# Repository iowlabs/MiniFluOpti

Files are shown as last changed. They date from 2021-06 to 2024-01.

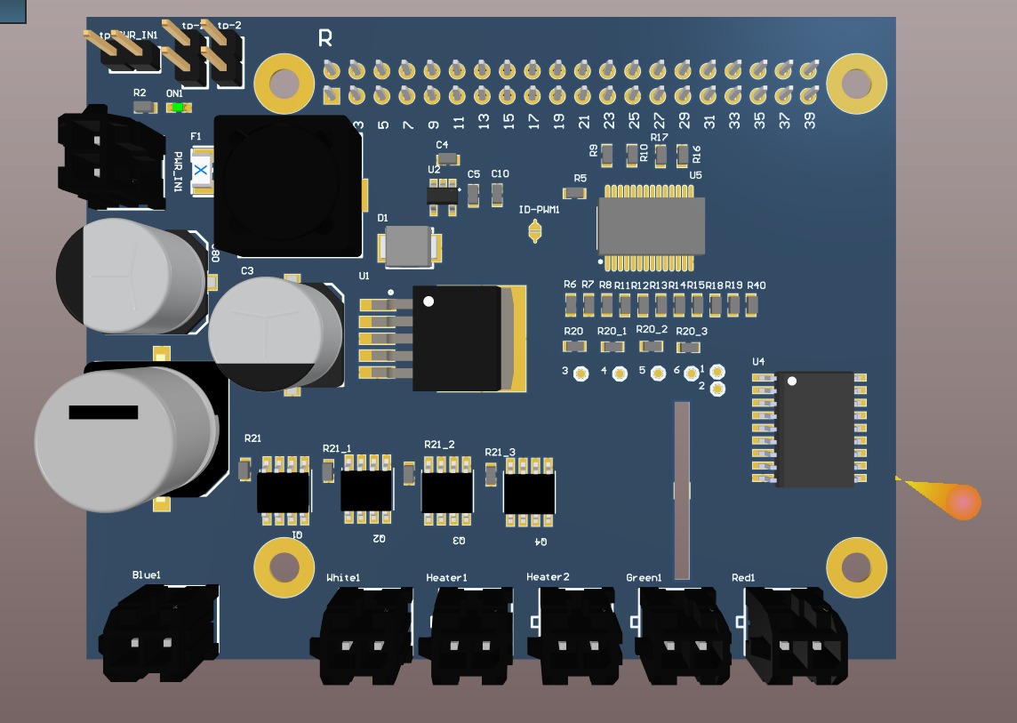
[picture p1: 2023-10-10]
hardware/Enclosure/Placa_esquematico.jpg

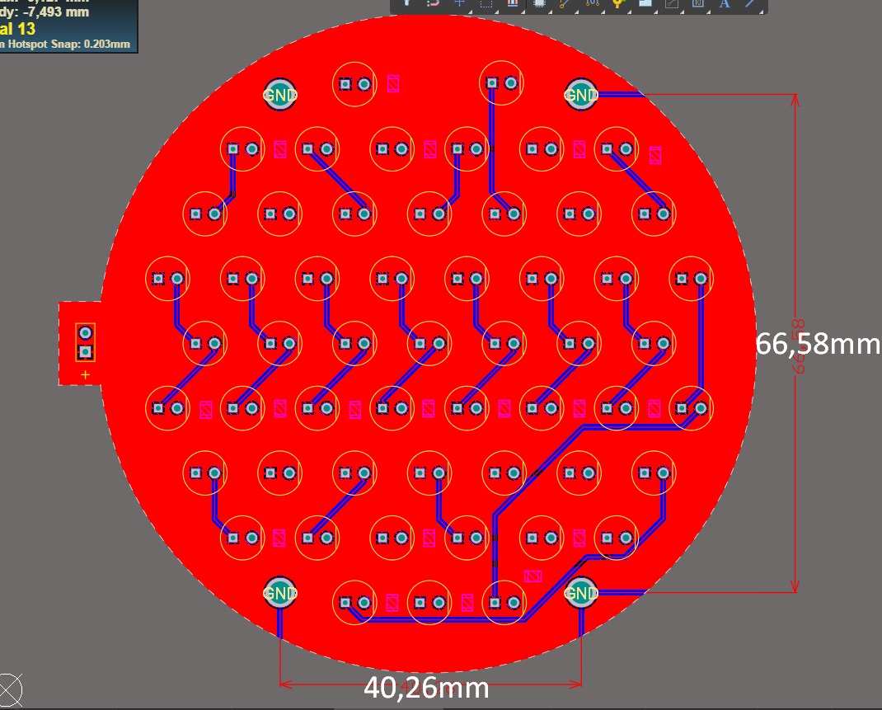
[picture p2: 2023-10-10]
hardware/Enclosure/Circle_LEDS_PCB.jpg

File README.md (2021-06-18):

# MiniFluOpti

Versión mini del proyecto FluOpti. Desarrollo conjunto con equipo docente del Instituto de Ingeniería Biológica UC. 
Este proyecto consiste en un controlador de LEDs configurable por I2C. La placa controla 4 canales controladores de LEDs, por medio de señales PWM generadas *on-board*. Los grupos de LEDs considerado para esta versión son: rojos, verde, azul y blanco. Adicionalmente la placa 
incluye un controlador de *heater* y un par de canales de lectura de sensores de temperatura del tipo termistor.

## Características:

* Voltaje de entrada 12[V].
* 4 Canales de salida LEDs: Rojo, Verde, Azul, Blanco.
* 1 Controlador de heater. Max: 12[V] - 3[A]
* 2 Canales de lector de termistor.
* Voltaje de salida para alimentar Rpi 5[V] 2.5[A] (Raspy 3b+)
* Voltaje en placa 3.3[V] para componentes digitales.
* Voltajes disponibles: 3.3[V] 5[V], 9[V] y 12[V]
* Protocolo de control: I2C (deseado)
 
Dependencias:
* Generador de PWMs PCA9685
* Drivers de corriente IRF740
* Drivers de baja corriente (500mA) ULN2803A
* Lector de termistor MAX6682
* Reguladores de voltaje
* Conversores DC-DC

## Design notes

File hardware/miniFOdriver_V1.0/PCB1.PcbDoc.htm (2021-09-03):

Reporting Options

# File in Newer Format

Date | : | 02-09-2021
Time | : | 23:33:18
Filename | : | C:\Users\Wac\Desktop\repo_pega\iowlabs\MiniFluOpti\3 - Hardware\miniFOdriver_V1.0\PCB1.PcbDoc

Version | Warning
Release 20.0 | CAUTION - Support of propagation delay for primitives
Release 20.0 | CAUTION - Support for PCB system parameters, used to contain additional data extracted from components

This file was generated by a later version of the software

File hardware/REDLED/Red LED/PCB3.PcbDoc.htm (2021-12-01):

Reporting Options

# File in Newer Format

Date | : | 19-10-2021
Time | : | 16:37:40
Filename | : | C:\Users\Wac\Desktop\repo_pega\iowlabs\MiniFluOpti\3 - Hardware\REDLED\Red LED\PCB3.PcbDoc

Version | Warning
Release 20.0 | CAUTION - Support of propagation delay for primitives
Release 20.0 | CAUTION - Support for PCB system parameters, used to contain additional data extracted from components

This file was generated by a later version of the software

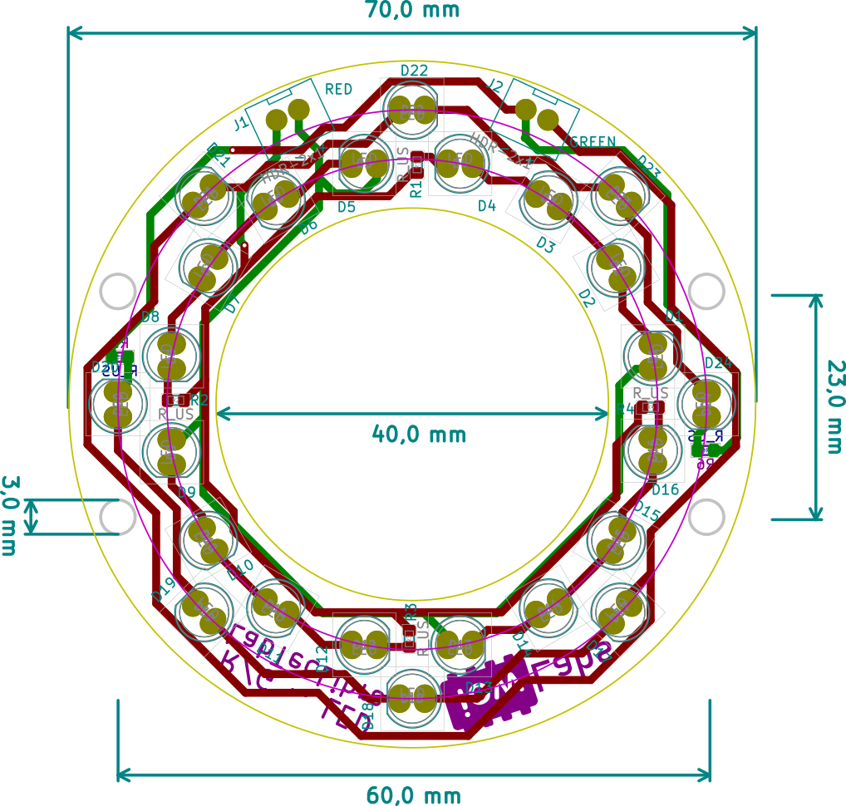
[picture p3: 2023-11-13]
hardware/GREENRED_LED/RG_Led_ring-brd.png

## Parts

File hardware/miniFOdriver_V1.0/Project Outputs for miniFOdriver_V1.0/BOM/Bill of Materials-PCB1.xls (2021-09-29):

Description | Designator | Footprint | Supplier Part Number 1 | Quantity | Supplier 1 | Value
Electrolytic Aluminium Capacitor | C2 | CAP_SMD_Electrolytic_10x10 | C178568 (https://octopart-clicks.com/click/altium?manufacturer=Panasonic&mpn=EEE-FK1V681AQ&seller=LCSC&sku=C178568&country=CL&channel=BOM%20Report) | 1 | LCSC | 680uF
Electrolytic Aluminium Capacitor | C3 | CAP_SMD_Electrolytic_10x10 | C249650 (https://octopart-clicks.com/click/altium?manufacturer=Loading...&mpn=Loading...&seller=LCSC&sku=C249650&country=CL&channel=BOM%20Report) | 1 | LCSC | 330uF
Capacitor (Semiconductor SIM Model) | C4, C5 | 1608[0603] | C59782 (https://octopart-clicks.com/click/altium?manufacturer=Samsung&mpn=CL10B105KO8NNNC&seller=LCSC&sku=C59782&country=CL&channel=BOM%20Report) | 2 | LCSC | 1uF
Capacitor (Semiconductor SIM Model) | C10 | 1608[0603] | C92487 (https://octopart-clicks.com/click/altium?manufacturer=Samsung&mpn=CL10A106MO8NQNC&seller=LCSC&sku=C92487&country=CL&channel=BOM%20Report) | 1 | LCSC | 10uF
Capacitor (Semiconductor SIM Model) | C12, C13 | 1608[0603] | C66501 (https://octopart-clicks.com/click/altium?manufacturer=Samsung&mpn=CL10B104KO8NNNC&seller=LCSC&sku=C66501&country=CL&channel=BOM%20Report) | 2 | LCSC | 100nF
Electrolytic Aluminium Capacitor | C80 | CAP_SMD_Electrolytic_5X5.4 |  | 1 | LCSC | 47uF
Schottky Diodes | D1 | SMB_L4.6-W3.6-LS5.3-RD | C180191 (https://octopart-clicks.com/click/altium?manufacturer=Loading...&mpn=Loading...&seller=LCSC&sku=C180191&country=CL&channel=BOM%20Report) | 1 | LCSC
Generic LED SMD | D2, D3, D4 | LED0603 | C72043 (https://octopart-clicks.com/click/altium?manufacturer=Loading...&mpn=Loading...&seller=LCSC&sku=C72043&country=CL&channel=BOM%20Report) | 3 | LCSC
SMD Fuse | F1 | F1206 | C310980 (https://octopart-clicks.com/click/altium?manufacturer=Loading...&mpn=Loading...&seller=LCSC&sku=C310980&country=CL&channel=BOM%20Report) | 1 | LCSC
solder jumper generic | ID-PWM1 | SJ2 |  | 1
Generic Header 2pos, 1 row, 2.54 pitch | J1, J2, J3, J4, J5, J6, J7, J8 | JST-2x1 | C20079 (https://octopart-clicks.com/click/altium?manufacturer=Loading...&mpn=Loading...&seller=LCSC&sku=C20079&country=CL&channel=BOM%20Report) | 8 | LCSC
Screw terminal 2pos, 1 row, 5pitch | J9 | T_BLOCK_2P | C8404 (https://octopart-clicks.com/click/altium?manufacturer=Kangnex&mpn=WJ126V-5.0-2P&seller=LCSC&sku=C8404&country=CL&channel=BOM%20Report) | 1 | LCSC
Inductor SMD | L1 | IND-SMD_L12.5-W12.5_SMDRS1275 | C439422 (https://octopart-clicks.com/click/altium?manufacturer=Loading...&mpn=Loading...&seller=LCSC&sku=C439422&country=CL&channel=BOM%20Report) | 1 | LCSC | 33uH
MOSFET N Channel 20V 8.7A 700mV @ 250uA 22mΩ @ 4.1A,4.5V SOIC-8_150mil RoHS | Q1, Q2, Q3, Q4 | SOIC8 | C169089 (https://octopart-clicks.com/click/altium?manufacturer=Infineon&mpn=IRF7402TRPBF&seller=LCSC&sku=C169089&country=CL&channel=BOM%20Report) | 4 | LCSC
GPIO Header for Raspberry Pi A+/B+/Pi 2/Pi 3 - 2x20 | R | rpi | 1568-1462-ND (https://octopart-clicks.com/click/altium?manufacturer=Loading...&mpn=Loading...&seller=LCSC&sku=1568-1462-ND&country=CL&channel=BOM%20Report) | 1 | LCSC
±1% ±100ppm/℃ 0.1W 220Ω 0603 Chip Resistor - Surface Mount ROHS, Resistor, Resistor, Resistor, Resistor, Resistor, Resistor | R1, R13, R14, R15, R18, R19, R40 | J1-0603 | C304718 (https://octopart-clicks.com/click/altium?manufacturer=Loading...&mpn=Loading...&seller=LCSC&sku=C304718&country=CL&channel=BOM%20Report) | 7 | LCSC | 220
Resistor | R2 | J1-0603 | C23057 (https://octopart-clicks.com/click/altium?manufacturer=Loading...&mpn=Loading...&seller=LCSC&sku=C23057&country=CL&channel=BOM%20Report) | 1 | LCSC | 442
Resistor | R3 | J1-0603 | C114608 (https://octopart-clicks.com/click/altium?manufacturer=Loading...&mpn=Loading...&seller=LCSC&sku=C114608&country=CL&channel=BOM%20Report) | 1 | LCSC | 150
Resistor | R5, R8, R9, R10, R11, R12 | J1-0603 | C105576 (https://octopart-clicks.com/click/altium?manufacturer=Loading...&mpn=Loading...&seller=LCSC&sku=C105576&country=CL&channel=BOM%20Report) | 6 | LCSC | 2K
Resistor | R6, R7, R16, R17 | J1-0603 | C441927 (https://octopart-clicks.com/click/altium?manufacturer=Panasonic&mpn=ERJPA3F1002V&seller=LCSC&sku=C441927&country=CL&channel=BOM%20Report) | 4 | LCSC | 10K
Resistor | R20, R20_1, R20_2, R20_3 | J1-0603 | C22781 (https://octopart-clicks.com/click/altium?manufacturer=Loading...&mpn=Loading...&seller=LCSC&sku=C22781&country=CL&channel=BOM%20Report) | 4 | LCSC | 110
Resistor | R21, R21_1, R21_2, R21_3 | J1-0603 | C25804 (https://octopart-clicks.com/click/altium?manufacturer=Uniroyal&mpn=0603WAF1002T5E&seller=LCSC&sku=C25804&country=CL&channel=BOM%20Report) | 4 | LCSC | 10K
 | R22, R23 | RESC1609X50X30LL10T20 | C170595 (https://octopart-clicks.com/click/altium?manufacturer=Loading...&mpn=Loading...&seller=LCSC&sku=C170595&country=CL&channel=BOM%20Report) | 2 | LCSC | 4.22k
Pin Header 2pos, 1 row, 2.54 pitch | tp-1, tp-2, tp-PWR_IN1 | HDR-TH_P2.54-H-M_A2541WV-2P | C492401 (https://octopart-clicks.com/click/altium?manufacturer=Loading...&mpn=Loading...&seller=LCSC&sku=C492401&country=CL&channel=BOM%20Report) | 3 | LCSC
Step-Down Positive Fixed 1 3A 150kHz TO-263-5 DC-DC Converters RoHS | U1 | TO-263-5 | C77782 (https://octopart-clicks.com/click/altium?manufacturer=Loading...&mpn=Loading...&seller=LCSC&sku=C77782&country=CL&channel=BOM%20Report) | 1 | LCSC
600mA CMOS LDO REGULATOR WITH ENABLE | U2 | SOT25-5 | C150742 (https://octopart-clicks.com/click/altium?manufacturer=Diodes&mpn=AP7365-33WG-7&seller=LCSC&sku=C150742&country=CL&channel=BOM%20Report) | 1 | LCSC
Darlington transistor array driver SOIC-18_300mi | U4 | SOIC18 | C33924 (https://octopart-clicks.com/click/altium?manufacturer=Loading...&mpn=Loading...&seller=LCSC&sku=C33924&country=CL&channel=BOM%20Report) | 1 | LCSC
LED Drivers,16CH, I2C, TSSOP-28 | U5 | SSOP-28_L | C92206 (https://octopart-clicks.com/click/altium?manufacturer=NXP%20Semiconductors&mpn=PCA9685PW%2FQ900%2C118&seller=LCSC&sku=C92206&country=CL&channel=BOM%20Report) | 1 | LCSC
Thermistor-to-Digital Converter, 10 Bits Temperature Resolution, -55 to 125 degC, 8-Pin SOP (U8+1), Pb-Free, Tape and Reel | U6, U7 | MAXM-U8+1_L | C2653145 (https://octopart-clicks.com/click/altium?manufacturer=Loading...&mpn=Loading...&seller=LCSC&sku=C2653145&country=CL&channel=BOM%20Report) | 2 | LCSC

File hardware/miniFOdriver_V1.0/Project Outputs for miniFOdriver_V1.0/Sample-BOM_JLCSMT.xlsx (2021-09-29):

Comment | Designator | Footprint | JLCPCB Part #（optional）
100uF | C1 | CAP-SMD_L3.5-W2.8 | C16133
15K | R5,R6 | R0603 | C22809
DC-005-20A_C136744 | DC1 | DC-IN-TH_DC-005-20A | C136744
Header-Female-2.54_1x8 | P2,P3 | HDR-TH_8P-P2.54-V | C27438
K2-1102DP-C4SW-04 | SW1 | KEY-TH_4P-L6.0-W6.0-P4.50-LS6.5 | C110153
ATMEGA328P-PU | U1 | DIP-28_L34.6-W7.3-P2.54-LS10.2-BL | C33901
670688000 | USB1 | USB-B-TH_67068-8000 | C114097

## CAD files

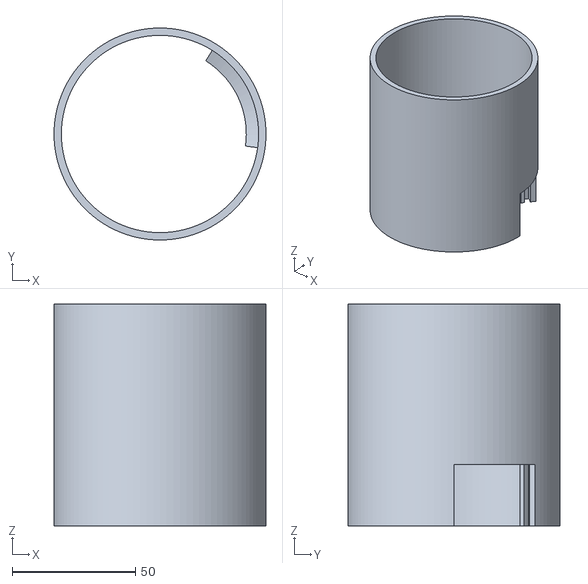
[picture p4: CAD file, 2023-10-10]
hardware/Enclosure/main_tube.stl
86.0 x 86.0 x 90.0

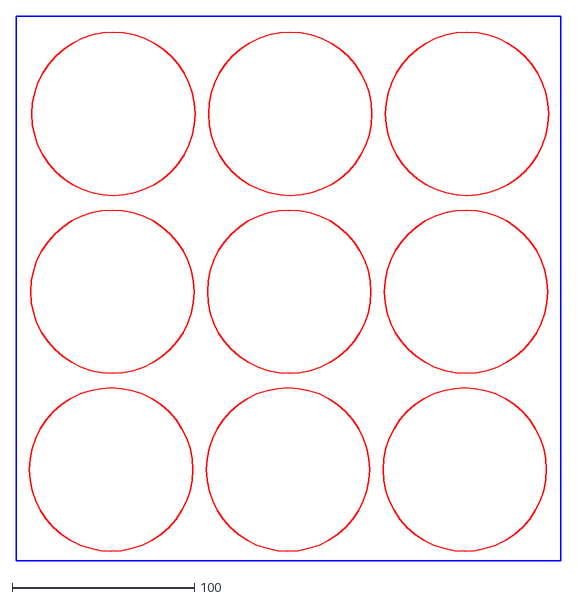
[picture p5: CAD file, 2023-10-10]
hardware/Enclosure/filters/blue_filtros.dxf
298.8 x 298.8

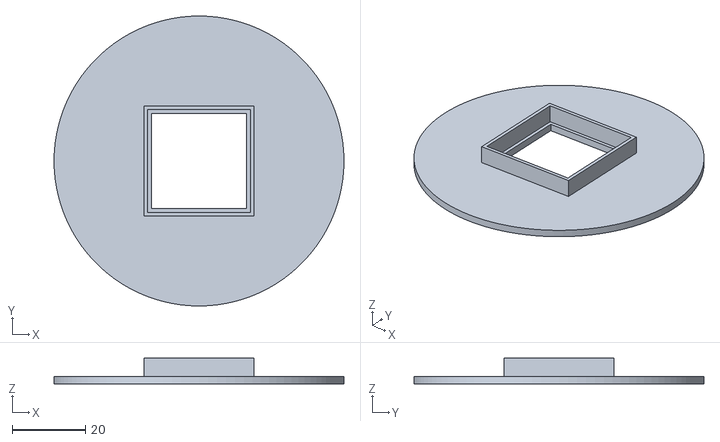
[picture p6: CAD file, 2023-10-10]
hardware/Enclosure/sample_holder_3x3.stl
79.0 x 79.0 x 7.00

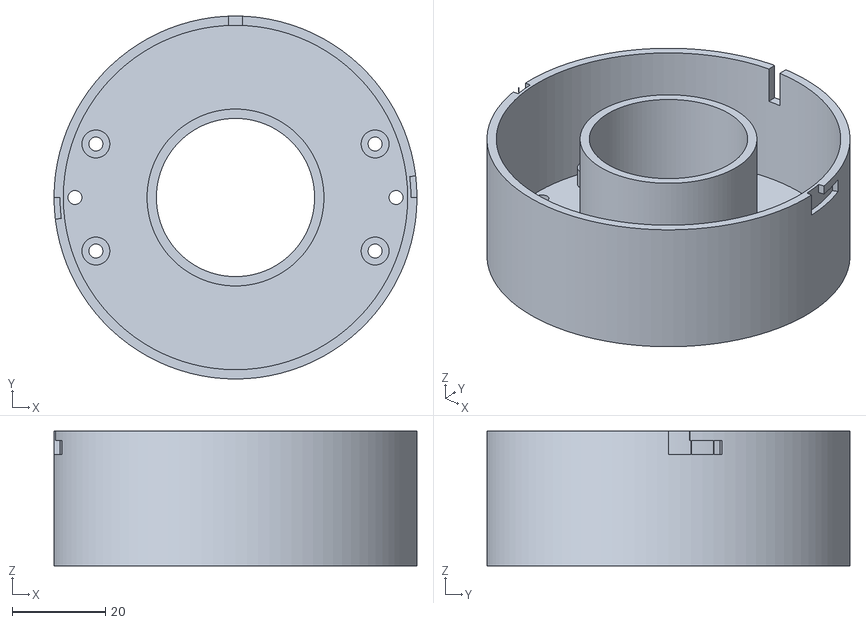
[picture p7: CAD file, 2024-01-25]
hardware/Enclosure/Soportes camara/STLs/Ring_enclosure.stl
78.0 x 78.0 x 29.0

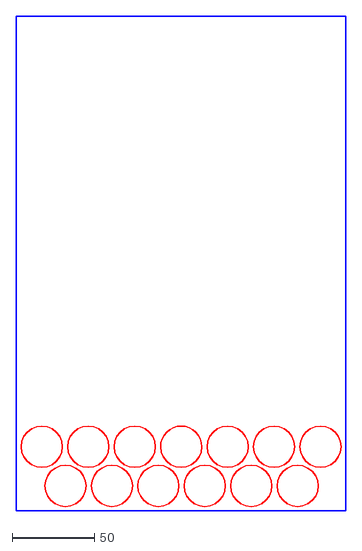
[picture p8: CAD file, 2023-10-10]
hardware/Enclosure/filters/ambar_filtros_13.dxf
200.0 x 300.0

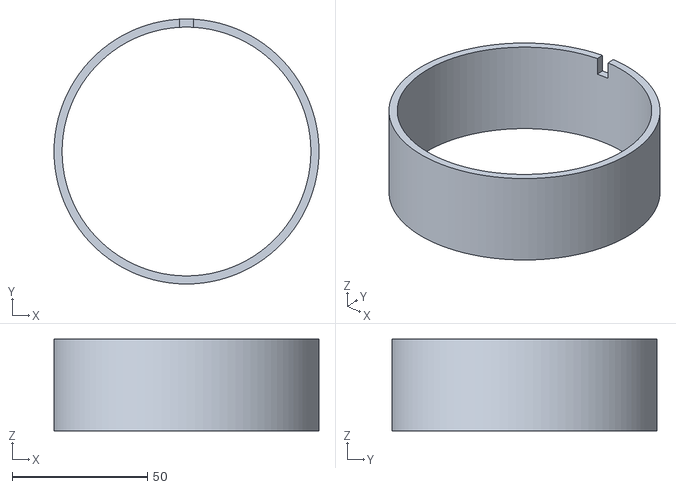
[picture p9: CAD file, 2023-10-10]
hardware/Enclosure/light_spacer.stl
98.0 x 98.0 x 34.0

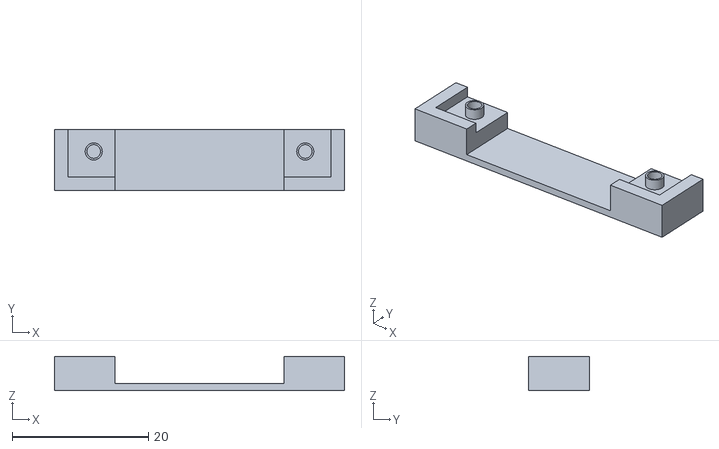
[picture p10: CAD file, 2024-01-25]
hardware/Enclosure/Soportes camara/STLs/HQ_test.stl
42.5 x 9.00 x 5.00

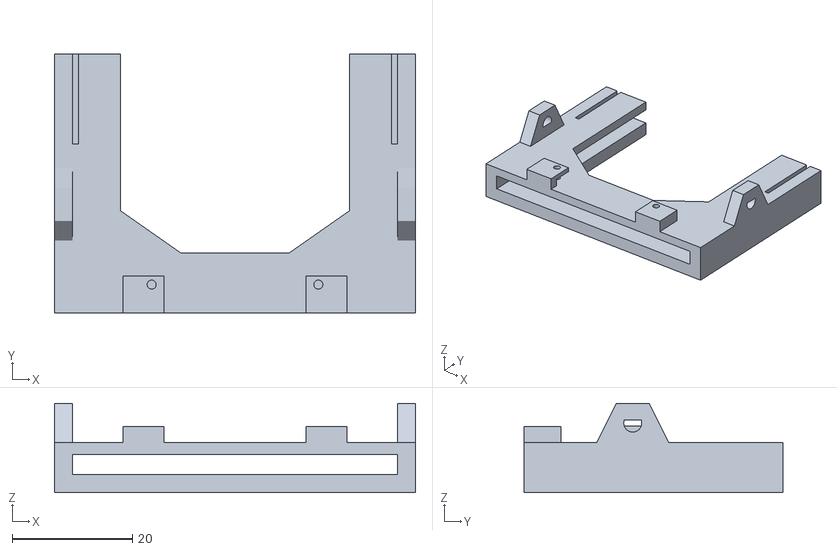
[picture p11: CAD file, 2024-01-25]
hardware/Enclosure/Soportes camara/STLs/Flat_cam_holder_WS_2.stl
60.0 x 43.1 x 14.8

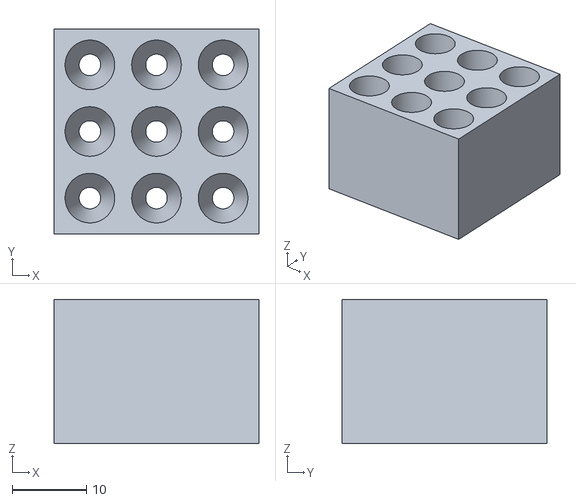
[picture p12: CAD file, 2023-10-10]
hardware/Enclosure/t_holder_3x3.stl
27.7 x 27.7 x 19.5

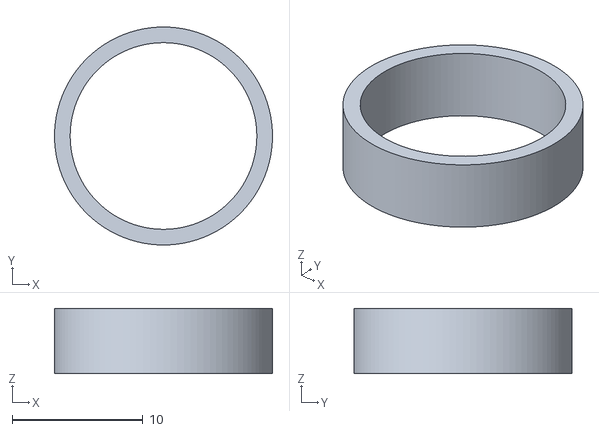
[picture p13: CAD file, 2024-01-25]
hardware/Enclosure/Soportes camara/STLs/M12_junction_test.stl
16.7 x 16.7 x 5.00

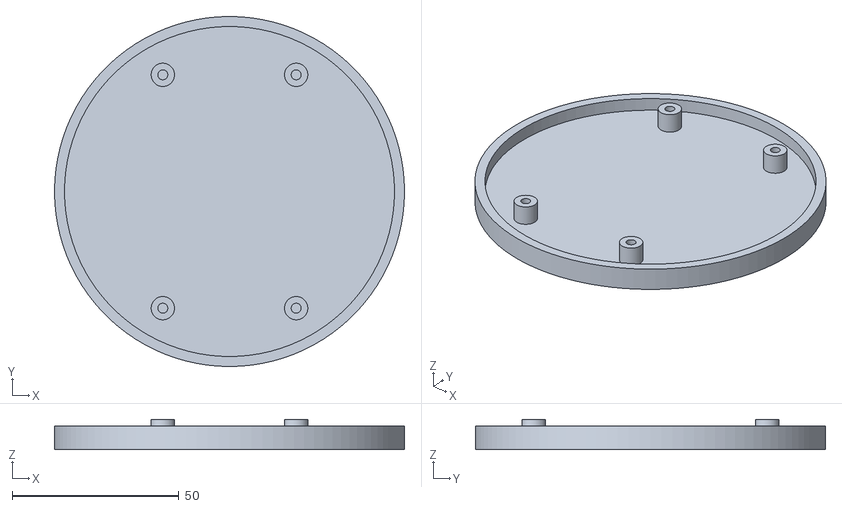
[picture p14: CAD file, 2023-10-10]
hardware/Enclosure/light_support.stl
105.0 x 105.0 x 9.00

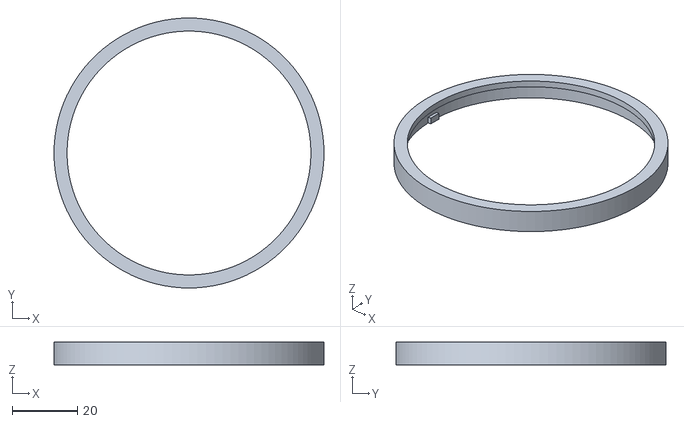
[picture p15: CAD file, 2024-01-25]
hardware/Enclosure/Soportes camara/STLs/outer_dring.stl
82.6 x 82.6 x 7.00

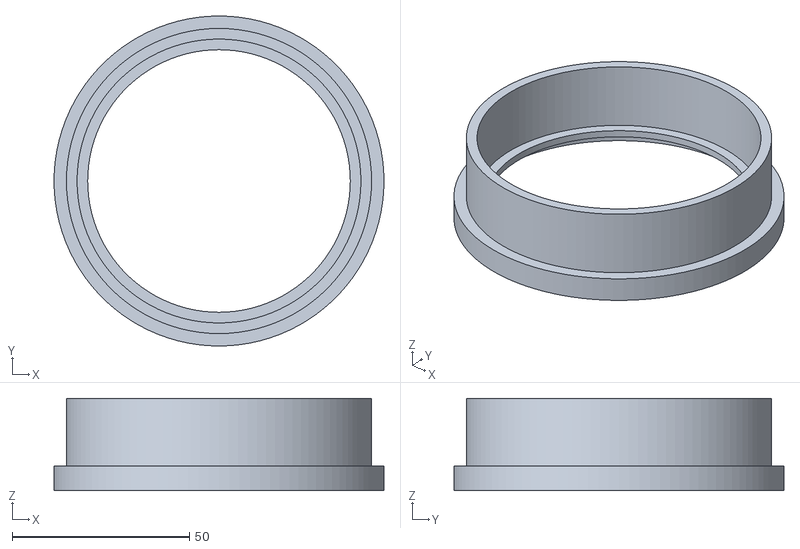
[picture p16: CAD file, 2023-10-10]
hardware/Enclosure/sample_tube.stl
93.0 x 93.0 x 26.0

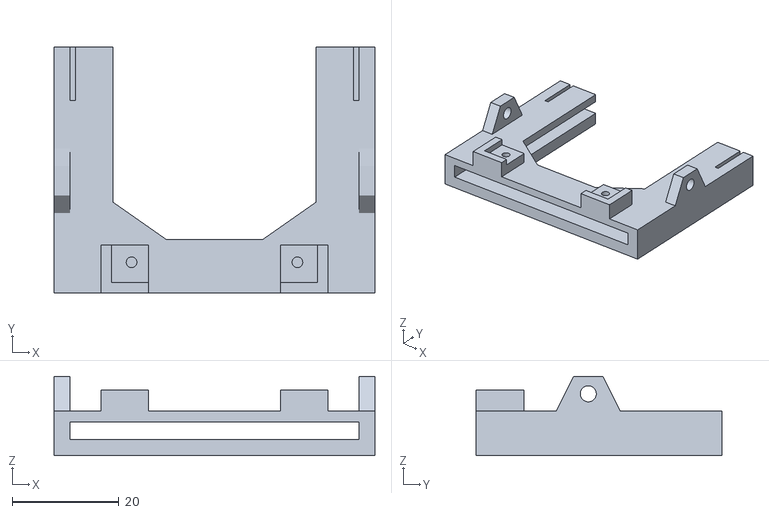
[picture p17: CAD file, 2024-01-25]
hardware/Enclosure/Soportes camara/STLs/Flat_cam_holder_HQ.stl
60.0 x 46.0 x 14.8

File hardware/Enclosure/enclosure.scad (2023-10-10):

/*
@Prosimio 2021

This is the Mini-FluOpti enclosure.

*/

////////////////
// Parameters //
////////////////


// general

id = 80;  // Internal diameter
ir = id/2; // internal radious

wt = 3;    // General wall thickness


// main tube 
os = 55;        // optical_space
cs = 35;        // camera_space
h1 = os + cs;   // main tube height
ha = 25;        // aperture height
h_door = ha + 4;  // door heigth
pih = h_door;       // pocket internal height
aa = 50;        // aperture angle [degrees]
pit = 3;        // pocket internal tickness
pet = 2;        // pocket external tickness
pia = 5;        // pocket internal angle [degrees]
pta = 3;        // pocket thickness angle [degrees]
ah = 10;        // door handle angle [degrees]

// sample tube
sh = 5;         // sheet height
st = 2;         // sheet support thickness
it = 3;         // internal sheet length
h2 = 21;        // tube height


// sample holder
hdt = 2;          // holder disk height
sst = 2;        // sample support sheet length
th = 2;         // barrier thickness horizontal
thz = 5;        // barrier thickness vertical       
xh = 28 ;   // x sample size + looseness if necessary
yh =  28 ;  // y sample size

// diffuser + filter support
f_t = 3;     // acrylic filter thickness
f_r = 45;        // filter radious
hd2 = 8;              // down mouting sheet heigh
hd1 = f_t + hd2;   // up mouting sheet heigh 
td = 2;                 // suppor disk thickness
ids = 1;                // internal disk sheet length
h3 = hd1 + hd2 + td;         // total piece height

// Light spacer
PCB_D = 90;         // PCB diameter
PCB_T = 11;         // PCB + LEDS thickness
PCB_support = 6;   // PCB support thickness
light_space = 17;   // Space between filter and LEDs
chx = 5;            // cable hole x dim
chz = 2.5;          // cable hole z dim
h4 = PCB_T + PCB_support + light_space;
ir_pcb = PCB_D/2 + 1; // 1 looseness  

// Light support
h5 = 4;             // sheet overlap height
scw_r = 1.5;          // screw radious
scw_t = 2;          // screw hole wall thickness
scw_sx = 40;         // screw separation in x axis
scw_sy = 70;         // screw separation in y axis
scw_h = 8;          // screw hole internal height
ls_r_int = ir_pcb + wt + 0.5; // 0.5 looseness

/////////////
// Display //
/////////////

//uncomment the objects to display them

//main_tube(h1,ir,wt, ha, aa, pia, pih, pta, pet, pit);
sample_tube(h2, sh, st, it, ir, wt);
//sample_holder(hdt, ir, sst, th, thz, xh, yh);
//filter_holder(ir_pcb,ir, f_r, hd1, hd2, f_t ,td ,wt ,ids);
//light_spacer(ir_pcb,h4,wt, chx, chz, h5);
//light_support(ls_r_int,wt,h5,scw_r,scw_t,scw_sx, scw_sy, scw_h,PCB_support);

//rotate_extrude(angle=90, convexity=10, $fn = 100)
//translate([10, 0]) polygon( points=[[0,0],[2,1],[2,0]] );

/////////////
// Modules //
/////////////

module main_tube(h, r, t, ha, aa, pia, pih, pta, pet, pit  ){
    
    // tube
    difference(){
        difference(){
        cylinder(h = h, r = r+t, $fn = 100, center = true);
        cylinder(h = h, r = r, $fn = 100, center = true);
        }
        
        // aperture
        rotate_extrude(angle=aa, convexity=10, $fn = 100)
        translate([r+t/2, -h/2+ha/2]) square(size = [t+1,ha],  center = true);
        }
    
    // pocket
    tih = pih+ha;   // total internal height
    teh = pih+ ha; //+ pet;   // total external height
    tia = aa + 2*pia; //total internal angle
    tea = aa + 2*pia + 2*pta; //total internal angle
    
    //pocket case
    difference(){
    rotate(a=[0,0,-pia - pta])
    rotate_extrude(angle=tea, convexity=10, $fn = 100)
    translate([r-(pit+pet)/2, -h/2+teh/2]) square(size = [pit+pet,teh],  center = true);
    
    //pocket hole
    rotate(a=[0,0,-pia])
    rotate_extrude(angle=tia, convexity=10, $fn = 100)
    translate([r-pit/2, -h/2+tih/2]) square(size = [pit,tih],  center = true);
    
    // aperture
    rotate_extrude(angle=aa, convexity=10, $fn = 100)
    translate([r-t, -h/2+ha/2]) square(size = [t+pit+pet,ha],  center = true);
    }
    
    // add triangle border to help printing
    tri_h = 3;   // triangle height
    rotate(a=[0,0,-pia - pta])
    rotate_extrude(angle=tea, convexity=10, $fn = 100)
translate([r-(pit+pet), -h/2+teh]) polygon( points=[[0,0],[pit+pet,tri_h],[pit+pet,0]] );
        
    
}

module door(){
    
        // door handle
rotate_extrude(angle=180, convexity=10, $fn = 100)
translate([10, 0]) polygon( points=[[0,0],[1,1],[0,1]] );
    }

module sample_tube(h, sh, st, it, r, t){
    
    swt = t + 0.5;  // +0.5 loseness
    
    she = sh+st; // external sheet height
    
    // main tube
    difference(){
    cylinder(h = h, r = r+t, $fn = 100, center = true);
    cylinder(h = h, r = r, $fn = 100, center = true);
    }
    
    // external sheet
    
    translate([0,0,-(h/2)])
    
        translate([0,0,-she/2+st])
        difference(){
        cylinder(h = she, r = r+swt+t, $fn = 100, center = true);
        cylinder(h = she, r = r+swt, $fn = 100, center = true);
        }

    // sample support disk
    translate([0,0,-(h/2-st/2)])
    difference(){
        cylinder(h = st, r = r+swt+t, $fn = 100, center = true);
        cylinder(h = st, r = r-it, $fn = 100, center = true);
        }
    
    
}


module sample_holder(h, r, st, t, tz, x, y){
    r = r - 0.5; // Looseness
    
    // disk
    difference(){
    cylinder(h = h, r = r, $fn = 100, center = true);
    cube(size = [x-st,y-st,h], center = true);
    }
    
    // holder
    translate([0,0,h/2+tz/2])
    difference(){
    cube(size = [x+t,y+t,tz], center = true);
    cube(size = [x,y,tz], center = true);
    }
}

module filter_holder(ru, rd, fr, h1, h2, ft ,t ,wt ,it){
    
    rui = ru + wt + 0.5; // 0.5 looseness
    rdi = rd + wt + 0.5; // 0.5 looseness
    
    // upper tube
    translate([0,0,(h1+t)/2])
    difference(){
    cylinder(h = h2, r = rui+wt, $fn = 100, center = true);
    cylinder(h = h2, r = rui, $fn = 100, center = true);
    }
    
    // filter tube
    translate([0,0,(ft+t)/2])
    difference(){
    cylinder(h = ft, r = rui+wt, $fn = 100, center = true);
    cylinder(h = ft, r = fr, $fn = 100, center = true);
    }
    // holder disk
    difference(){
    cylinder(h = t, r = fr+wt, $fn = 100, center = true);
    cylinder(h = t, r = rdi-it, $fn = 100, center = true);
    }
    
    // down tube
    translate([0,0,-(h2+t)/2])
    difference(){
    cylinder(h = h2, r = rdi+wt, $fn = 100, center = true);
    cylinder(h = h2, r = rdi, $fn = 100, center = true);
    }
}

module light_spacer(r,h,wt, cx, cz, h_sheet){
    hh = cz + h_sheet;  // hole height
    
    difference(){
        // Tube
        cylinder(h = h, r = r+wt, $fn = 100, center = true);
        cylinder(h = h, r = r, $fn = 100, center = true);
        
        // Hole
        translate([0,r+wt/2,+h/2-hh/2])
        cube([cx,wt+1,hh],center=true);
        // wt + 1 to give looseness
    }
    
}

module light_support(r, wt, h, sr, st, ssx, ssy, sih,seh){
    // sih = screw hole internal height
    // seh = screw support external height
    // ssx = screw spacer x axis
    // ssy = screw spacer y axis
    
    // base disk + supports
    difference(){
    union(){
    translate([0,0,wt/2])
    cylinder(h = wt, r = r+wt, $fn = 100, center = true);
        
    //supports
    for (x =[-ssx/2,ssx/2]){
        for (y =[-ssy/2,ssy/2]){
            translate([x,y,seh/2+wt])
            cylinder(h = seh, r = sr+st, $fn = 100, center = true);
            }
    }
          };
    // Holes
    union(){
        for (x =[-ssx/2,ssx/2]){
            for (y =[-ssy/2,ssy/2]){
                translate([x,y,seh/2+wt])
                // it is translated accord the support
                cylinder(h = sih, r = sr, $fn = 100, center = true);
                }
         }
        }
    }
    // screw supports
    /*
    for (x =[-ss/2,ss/2]){
        for (y =[-ss/2,ss/2]){
            translate([x,y,seh/2+wt])
            difference(){
            cylinder(h = seh, r = sr+st, $fn = 100, center = true);
            cylinder(h = seh, r = sr, $fn = 100, center = true);
            }
        }
    }
    */
    
    // overlap tube sheet
    translate([0,0,h/2+wt])
    difference(){
        // Tube
        cylinder(h = h, r = r+wt, $fn = 100, center = true);
        cylinder(h = h, r = r, $fn = 100, center = true);
        
    }
    
    
}
    

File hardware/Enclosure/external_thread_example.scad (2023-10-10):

use <threadlib/threadlib.scad>

/*
Table:
https://github.com/adrianschlatter/threadlib/blob/develop/THREAD_TABLE.scad
*/


// mode 1
/*
t = 5;       // turns
p = 0.7;    // pitch --> first parameter of table
h = (t+1)*0.7;

difference(){
translate([0,0,p/2])
bolt("M4", turns=t);
translate([0,0,h/2])
cylinder(h = h, r = 1, $fn = 100, center = true);
}
*/


name = "M24-ext";
specs = thread_specs(name);
P = specs[0];               // Pitch
Rrot = specs[1]; 
Dsupport = specs[2];
section_profile = specs[3];     // Diameter

T =5; // turns
H = (T + 1) * P;

// create Thread

difference(){
translate([0,0,P/2])
union(){
thread(name, turns=T);
translate([0, 0, -P / 2])
cylinder(h=H, d=Dsupport, $fn=120);
}
cylinder(h=H, d=Dsupport-1, $fn=120);
}

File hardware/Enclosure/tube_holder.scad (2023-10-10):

/*
@Prosimio 2021

This a PCR-tube holder generator.
It was designed to be used in the FluoPi Machine but
can be used for other purposes.

*/

////////////////
// Parameters //
////////////////


// Tube dimentions

h1 = 8.5;
h2 = 11;
h3 = 0.5;

H = h1 + h2 + h3;  // total tube height

d1 = 6.3 + 0.4; // 0.2 looseness
d2 = 2.6 + 0.3; // 0.1 looseness


// Box holder

box_thick = 3;   // external thickness

box_x = d1 + box_thick;
box_y = d1 + box_thick;
box_z = H - h3 ; // left the tip outside

pitch = 9;   // Separation between holes center
n = 3;
m = 3;

// create holder

holder(n,m,pitch,box_x,box_y,box_z, H, h1, h2, h3, d1, d2);



// uncomment to display the tube
//tube(H, h1, h2, h3, d1, d2);

/*
difference(){
    box(box_x, box_y, box_z, h3);
    tube(H, h1, h2, h3, d1, d2);
}
/*/

/////////////
// Modules //
/////////////

module tube(H, h1, h2, h3, d1, d2){
    
    // top section
    translate([0,0,H-h1/2])
    cylinder(h = h1, r1 = d1/2, r2 = d1/2, $fn = 100, center = true);
    
    // middle section
    translate([0,0, H-h1-h2/2])
    cylinder(h = h2, r1 = d2/2, r2 = d1/2, $fn = 100, center = true);
    
    // down section
    translate([0,0, h3/2])
    cylinder(h = h3, r1 = d2/2, r2 = d2/2, $fn = 100, center = true);
    
}

module box(x,y,z,h3){
    translate([0,0,z/2+h3])
    cube(size = [x, y, z], center = true);
    
}

// n and m are the holder grid dimentions
module holder(n,m,p,bx,by,bz, H, h1, h2, h3, d1, d2){
    
    for (i =[0:n-1]){
        for (j =[0:m-1]){
            translate([i*p,j*p,0])
            difference(){
            box(bx, by, bz, h3);
            tube(H, h1, h2, h3, d1, d2);
            }
        }
    }
        
    
    
}

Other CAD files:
hardware/Enclosure/Soportes camara/STLs/inner_dring.stl
hardware/Enclosure/tube_holder.stl
hardware/Enclosure/filter_holder.stl
hardware/Enclosure/Soportes camara/STLs/lens_remove.stl
hardware/Enclosure/Soportes camara/Flat_cam_holder.scad
hardware/Enclosure/Soportes camara/STLs/Flat_cam_holder_V2.stl
hardware/Enclosure/Soportes camara/STLs/Flat_cam_holder_WS.stl
hardware/Enclosure/Soportes camara/STLs/Focus_knob_RPIv2.stl
hardware/Enclosure/Soportes camara/STLs/Focus_knob_WS.stl
hardware/Enclosure/Soportes camara/STLs/V2_cam_holder_test.stl
hardware/Enclosure/Soportes camara/STLs/V2_filter_holder_thread.stl
hardware/Enclosure/Soportes camara/STLs/ring_arm.stl
hardware/Enclosure/Soportes camara/V2_filter_holder_thread.scad
hardware/Enclosure/Soportes camara/white_light_module.scad

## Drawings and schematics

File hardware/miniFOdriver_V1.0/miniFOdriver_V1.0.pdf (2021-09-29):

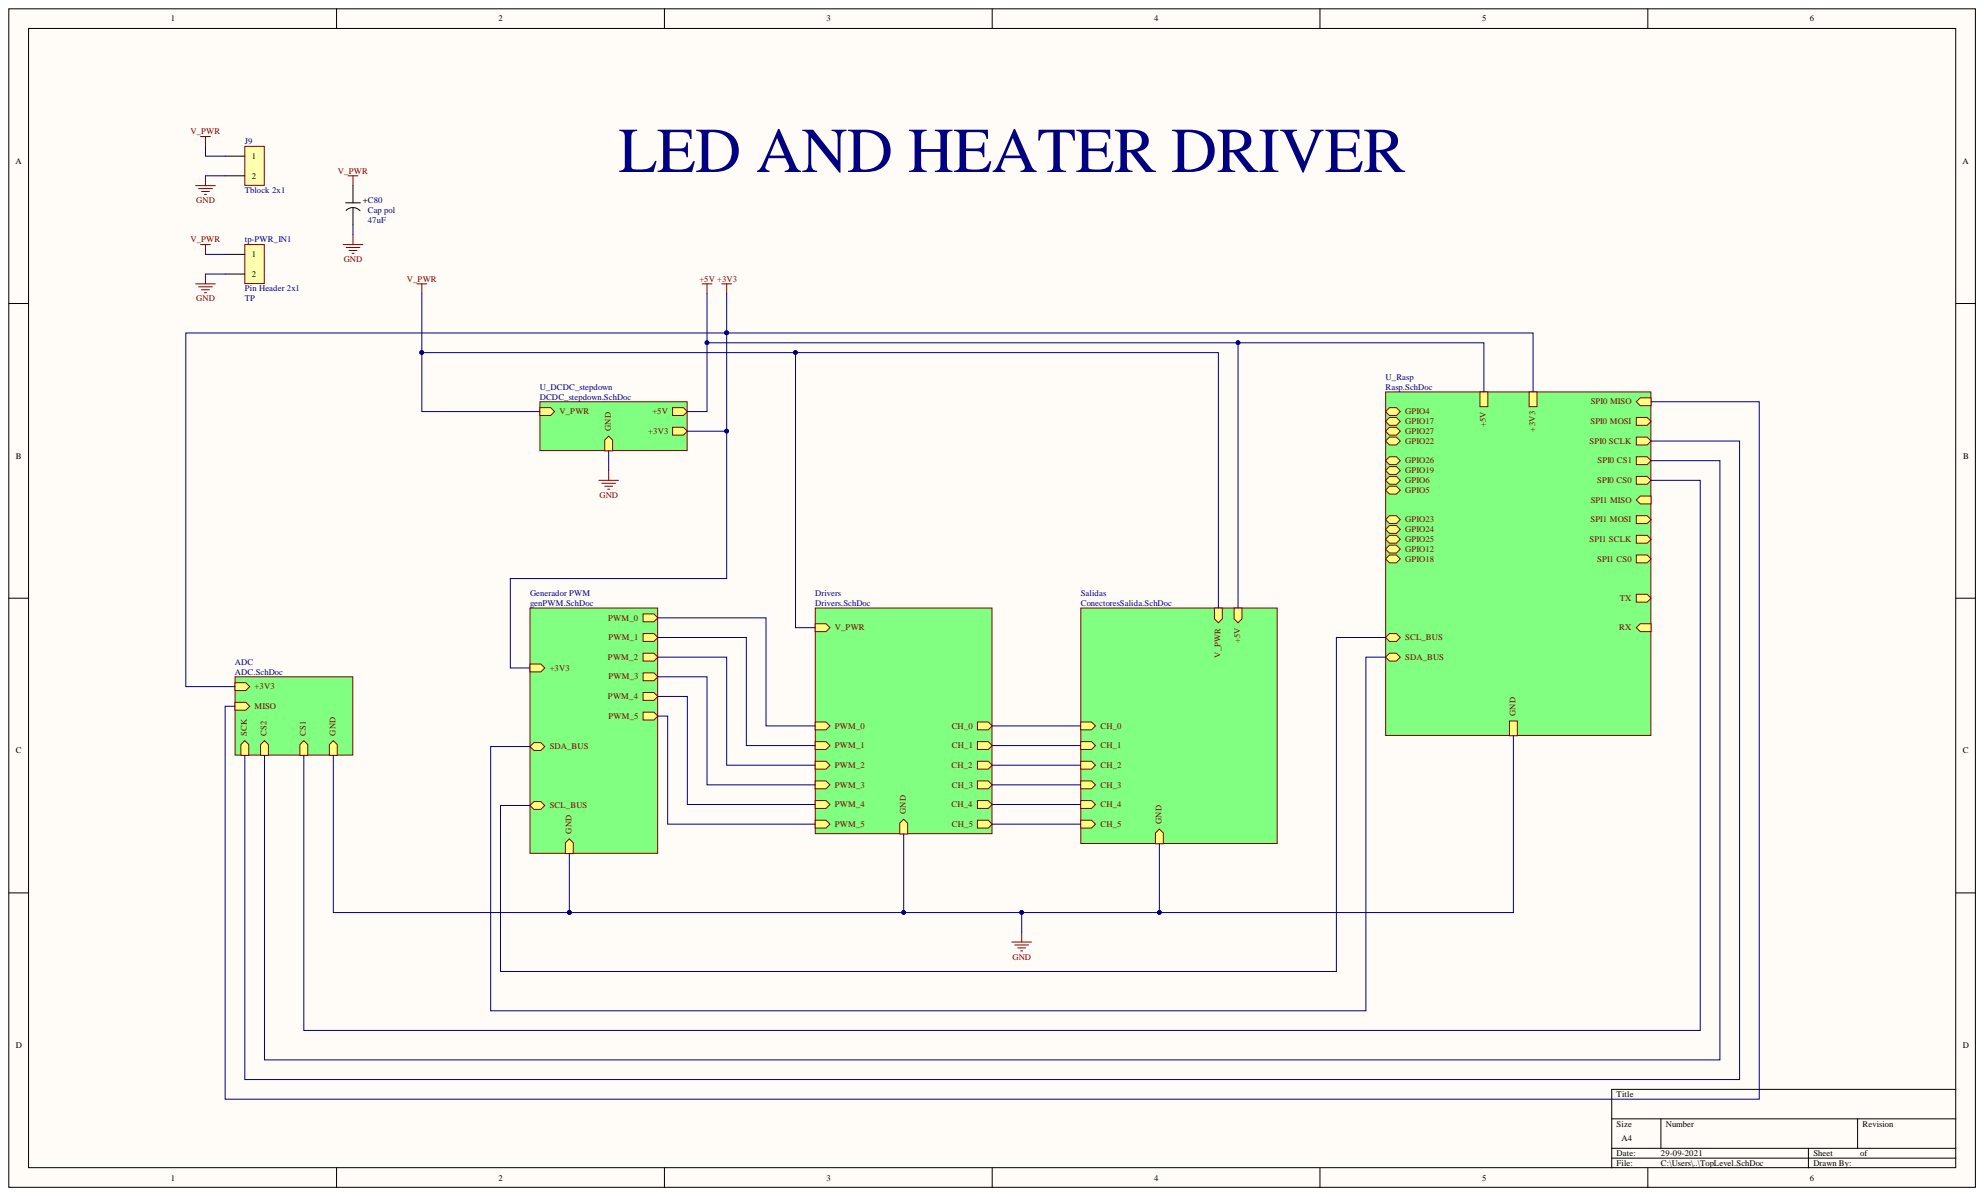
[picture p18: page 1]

LED AND HEATER DRIVER

U_Rasp Rasp.SchDoc

GPIO4 GPIO17 SPI0 MOSI GPIO27 GPIO22 SPI0 SCLK

GPIO26 SPI0 CS1
GPIO19 GPIO6 SPI0 CS0

GND | Drivers Salidas Drivers.SchDoc ConectoresSalida.SchDoc | GPIO5 SPI1 MISO GPIO23 SPI1 MOSI GPIO24 GPIO25 SPI1 SCLK GPIO12 GPIO18 SPI1 CS0 TX RX SCL_BUS SDA_BUS

PWM_0 PWM_1 PWM_2 +3V3 PWM_3 PWM_4 PWM_5 SDA_BUS | V_PWR PWM_0 CH_0 PWM_1 CH_1 PWM_2 CH_2 PWM_3 CH_3 PWM_4 CH_4 PWM_5 CH_5 | CH_0

+3V3 MISO

SCL_BUS

Size A4 | Number | Revision

Date: 29-09-2021 | Sheet of
File: C:\Users\..\TopLevel.SchDoc | Drawn By:

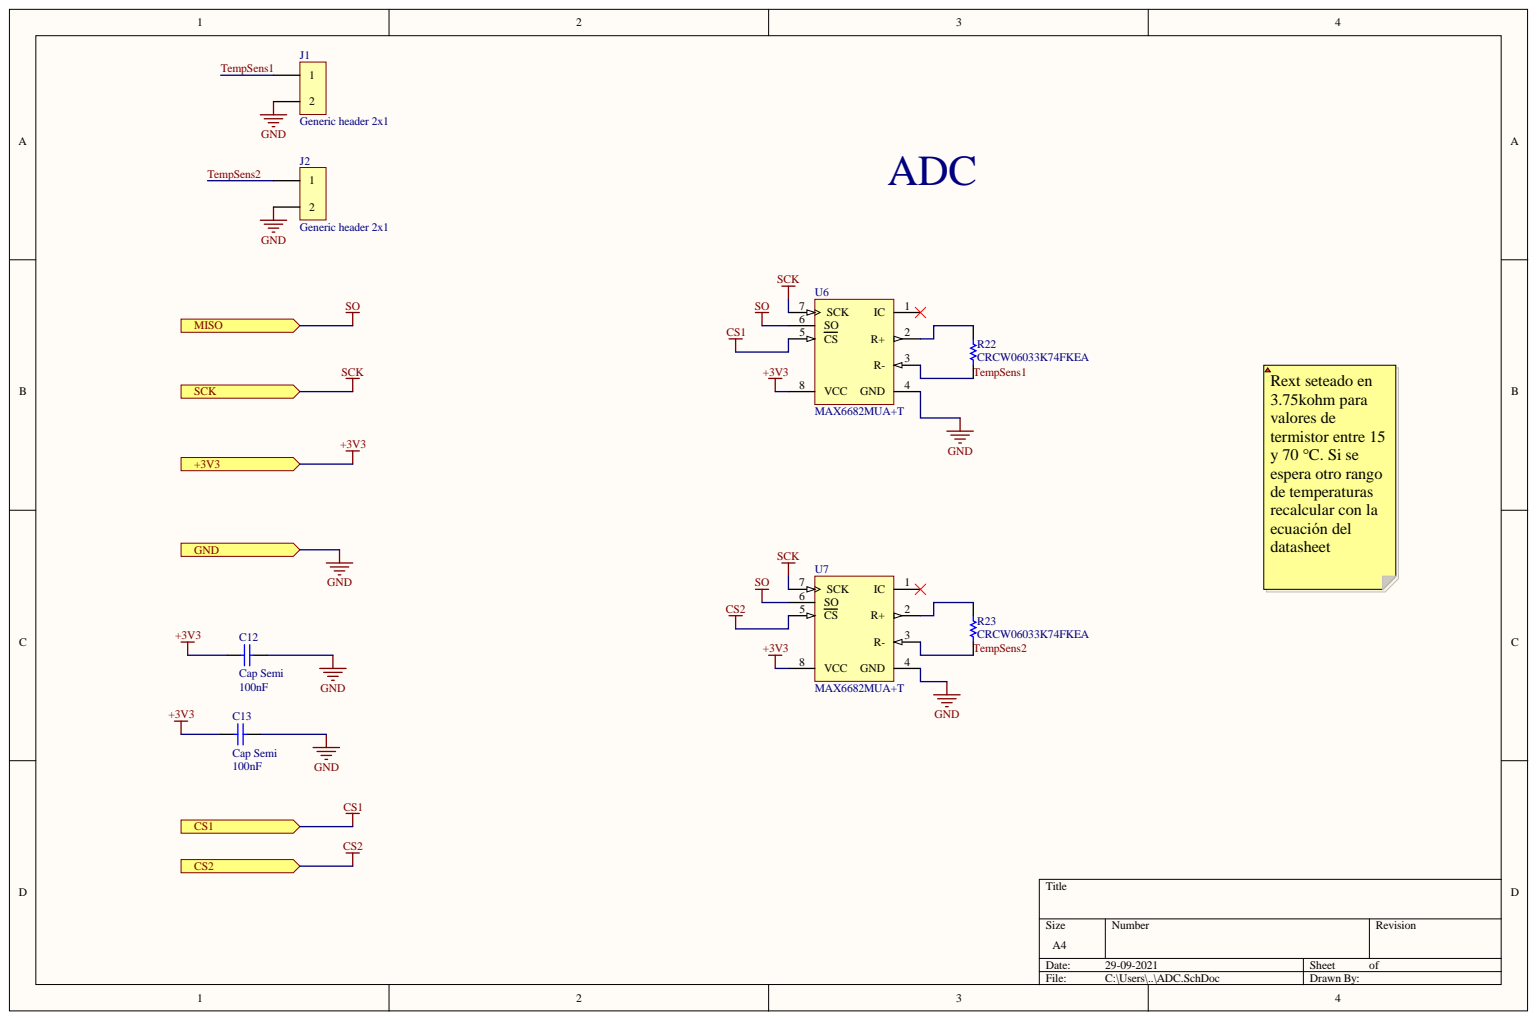
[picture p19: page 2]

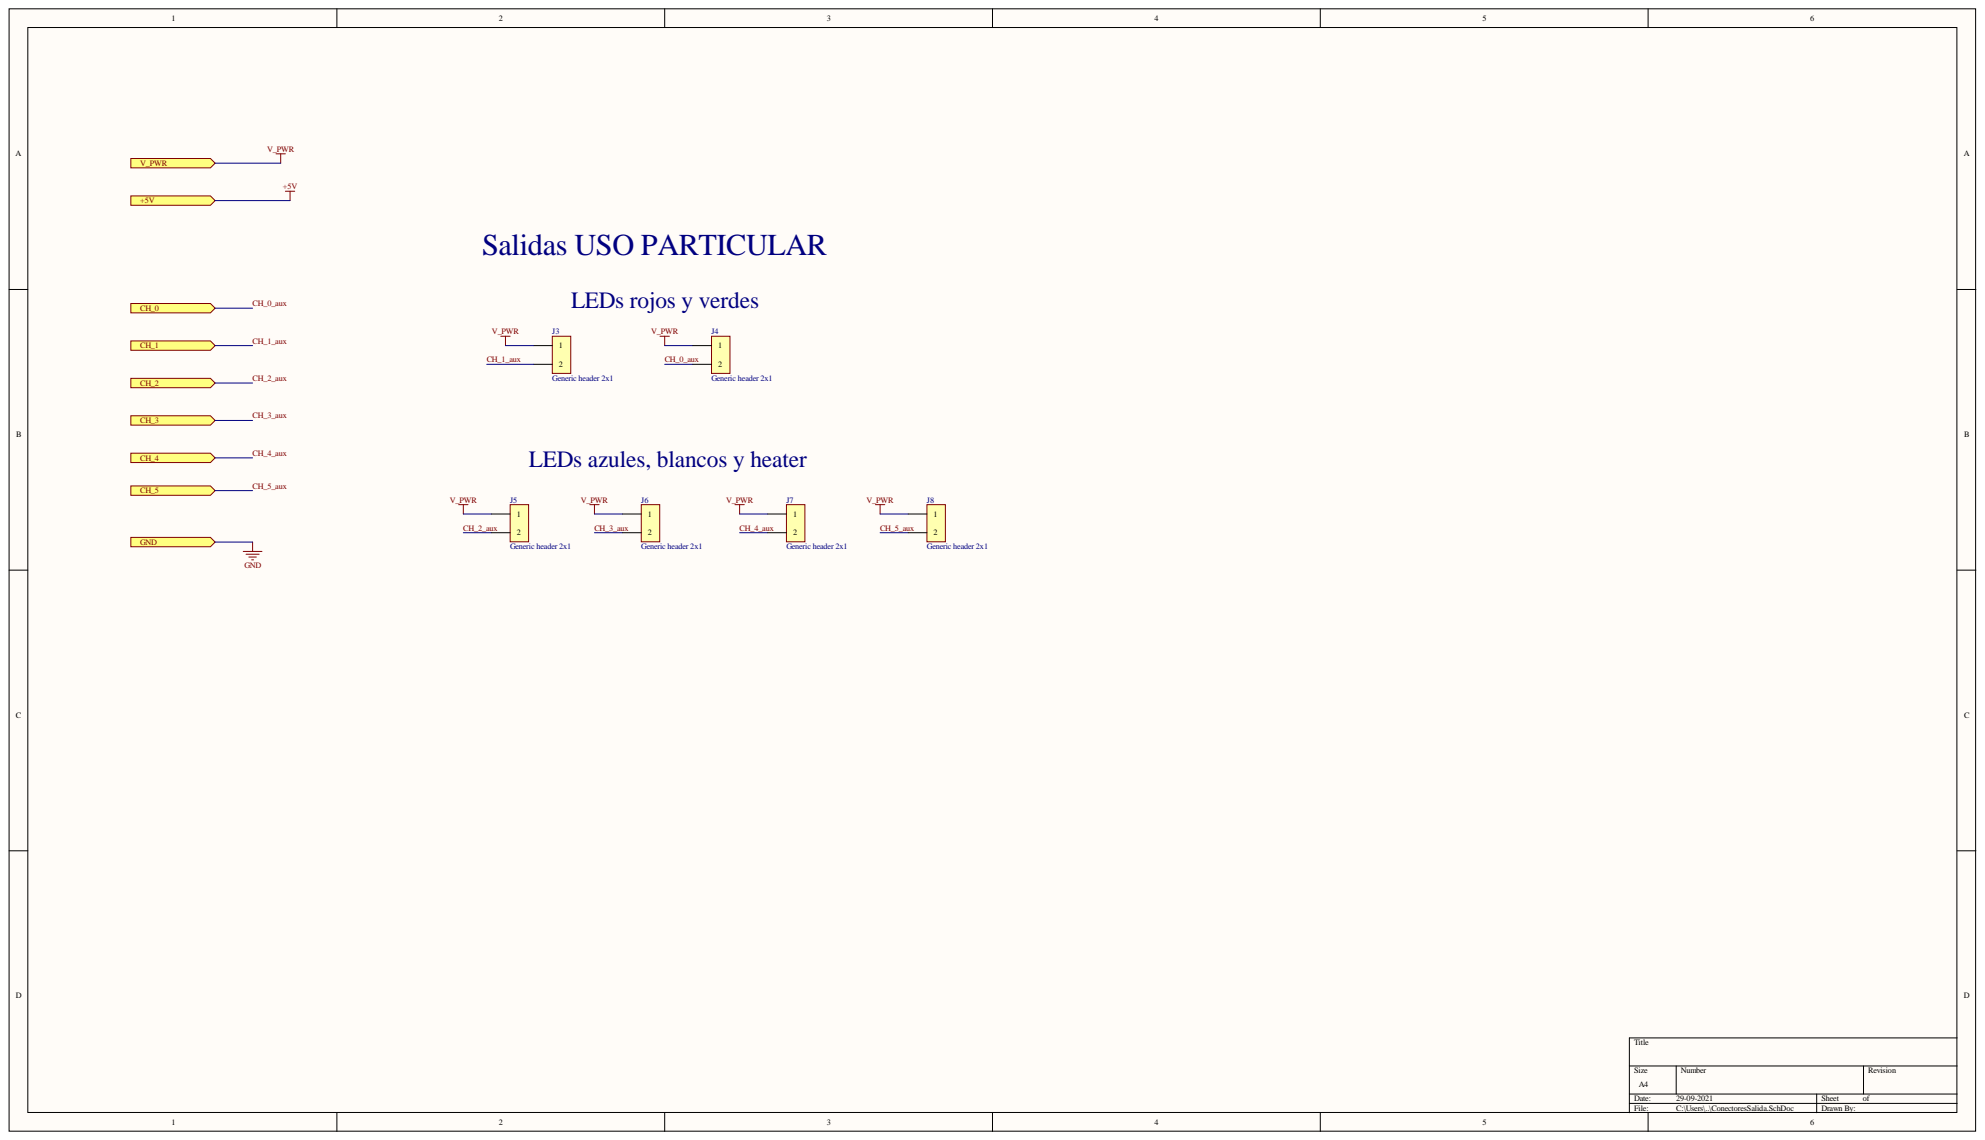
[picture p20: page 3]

LEDs azules, blancos y heater

Size A4 | Number | Revision

Date: 29-09-2021 | Sheet of
File: C:\Users\..\ConectoresSalida.SchDoc | Drawn By:

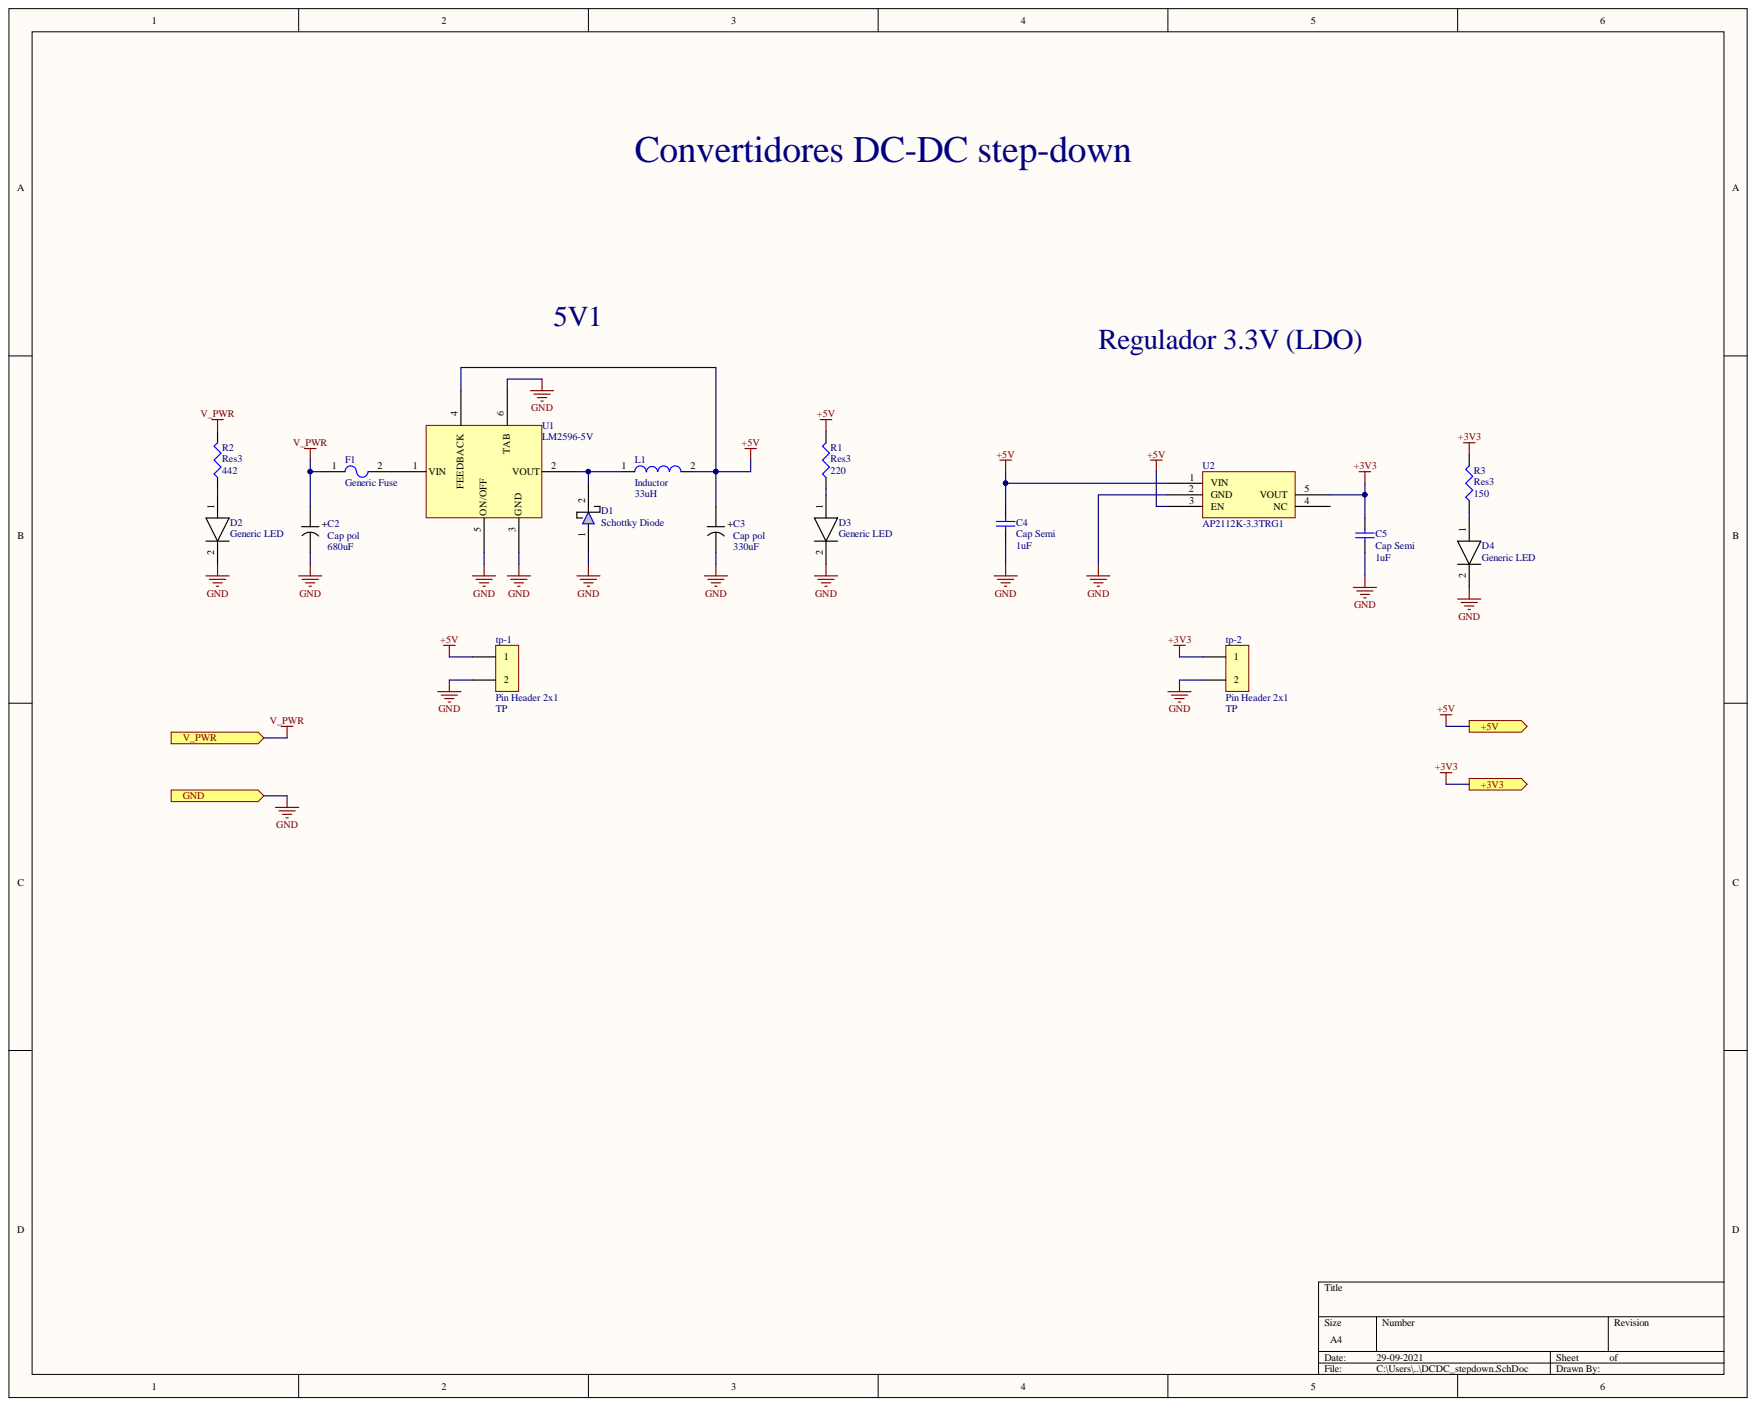
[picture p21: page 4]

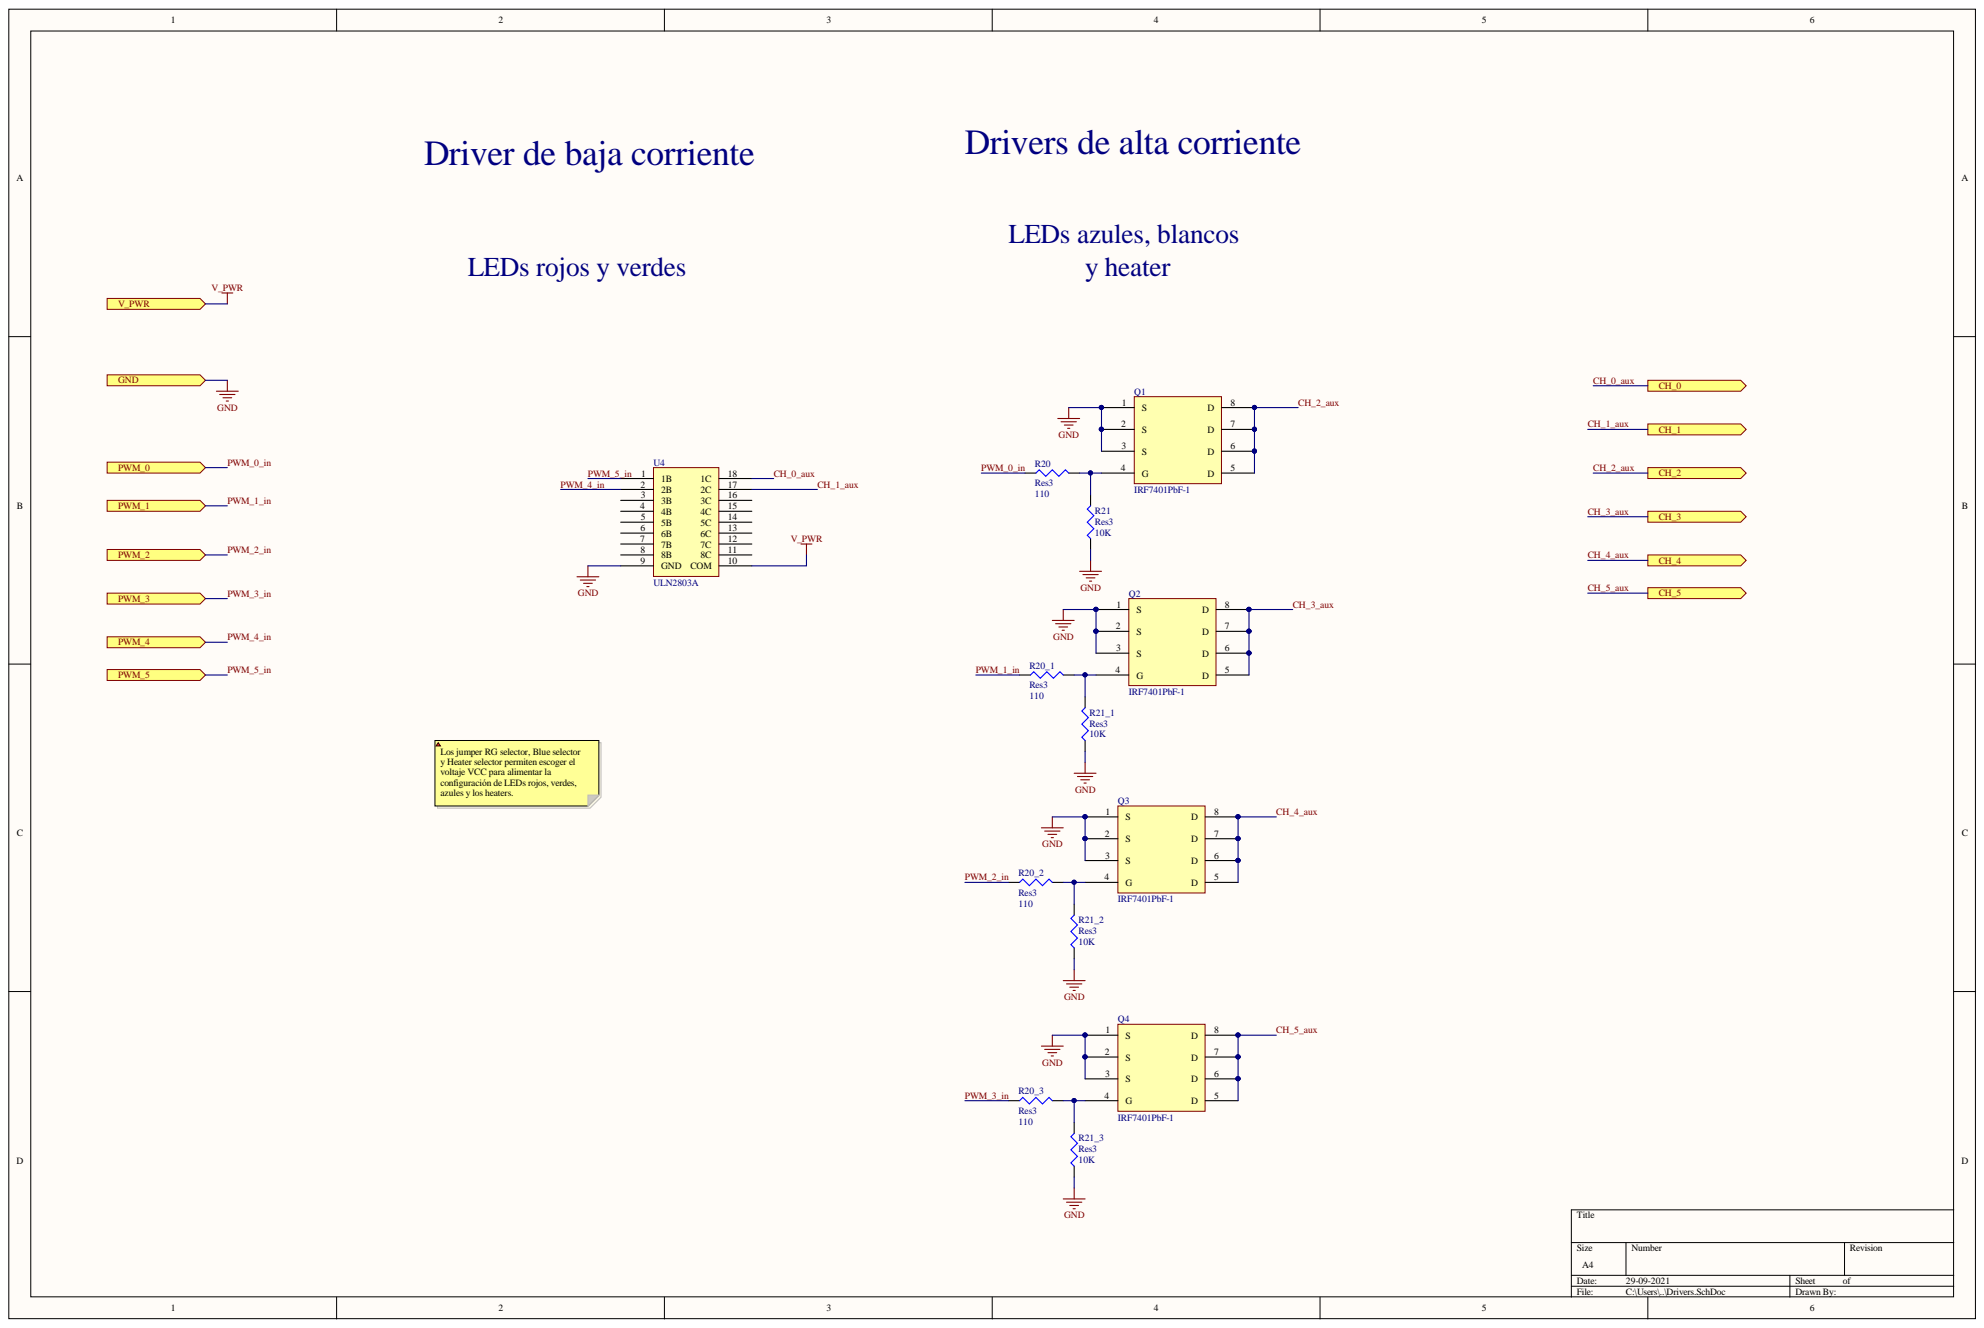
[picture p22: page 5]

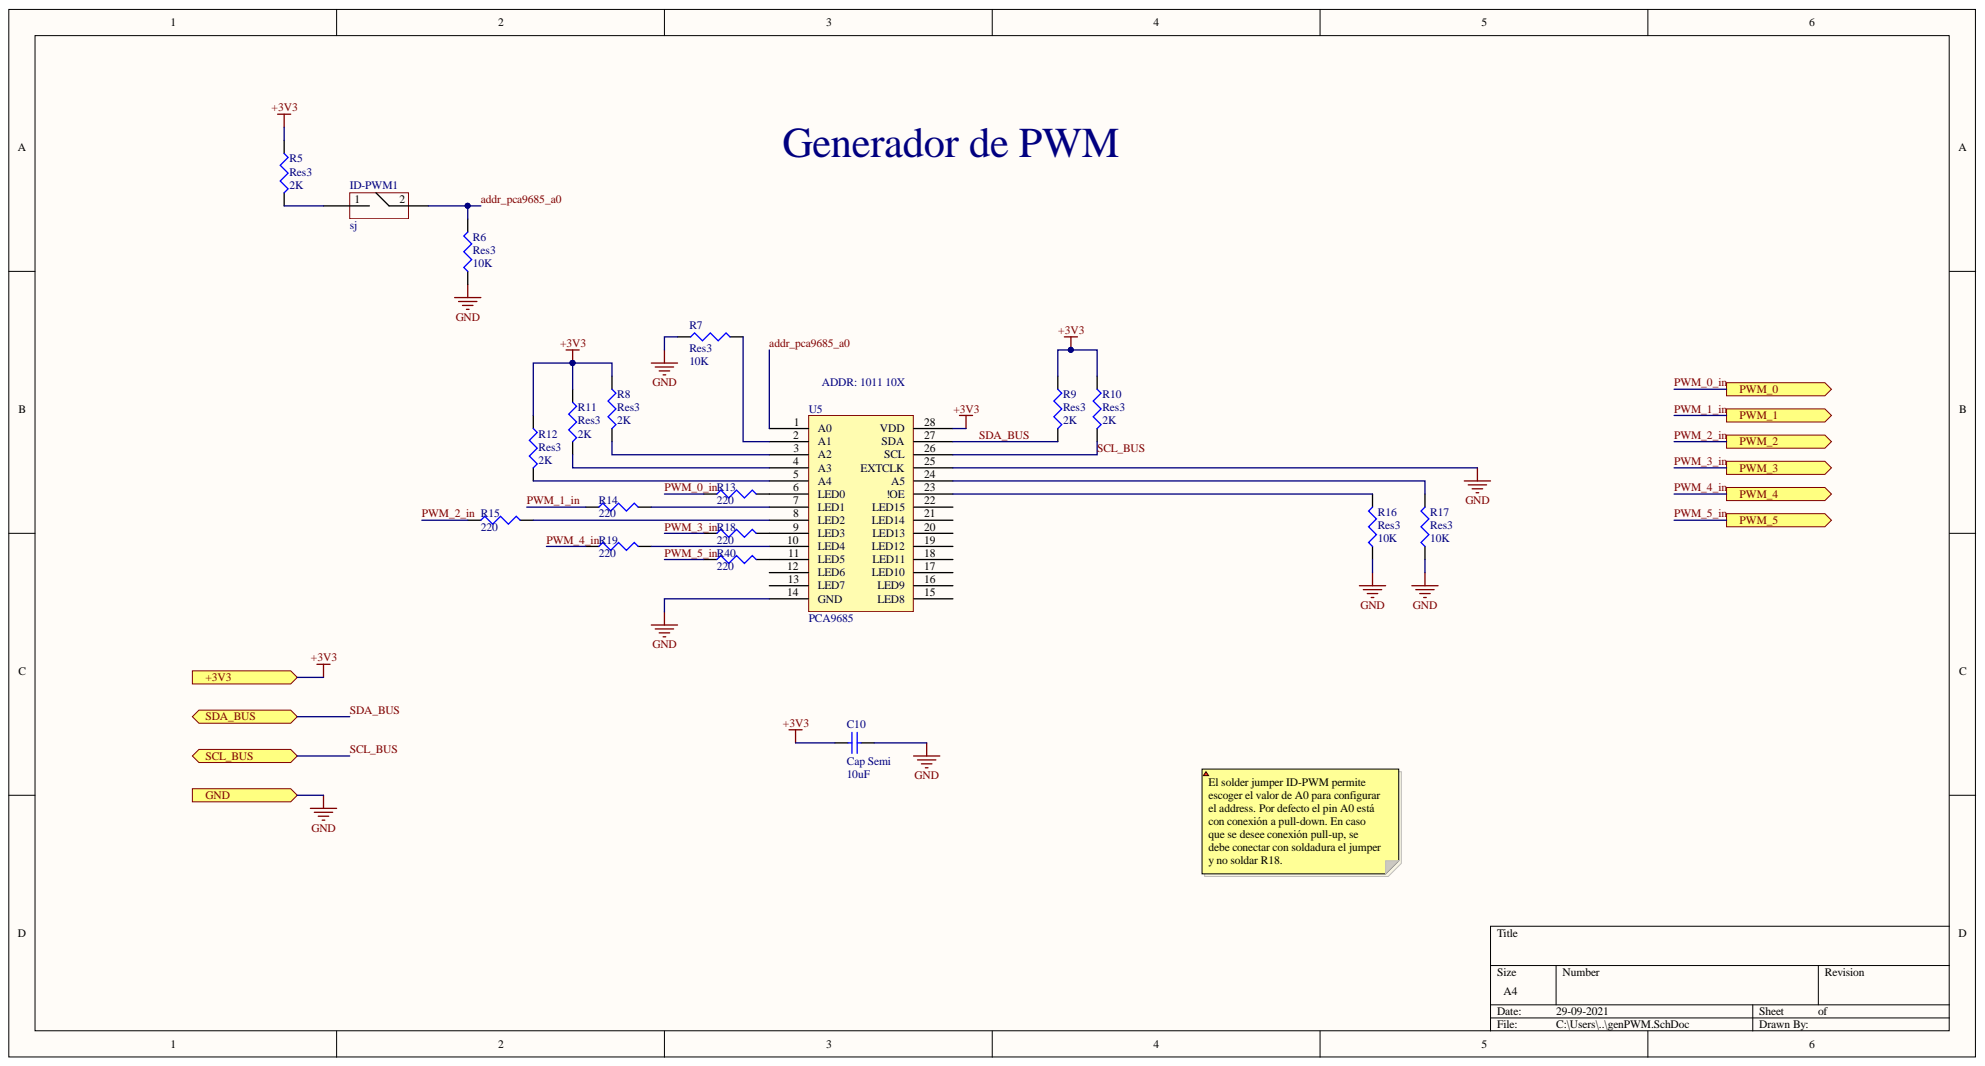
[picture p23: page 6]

El solder jumper ID-PWM permite
escoger el valor de A0 para configurar
el address. Por defecto el pin A0 está
con conexión a pull-down. En caso
que se desee conexión pull-up, se
debe conectar con soldadura el jumper
y no soldar R18.

Size A4 | Number | Revision

Date: 29-09-2021 | Sheet of
File: C:\Users\..\genPWM.SchDoc | Drawn By:

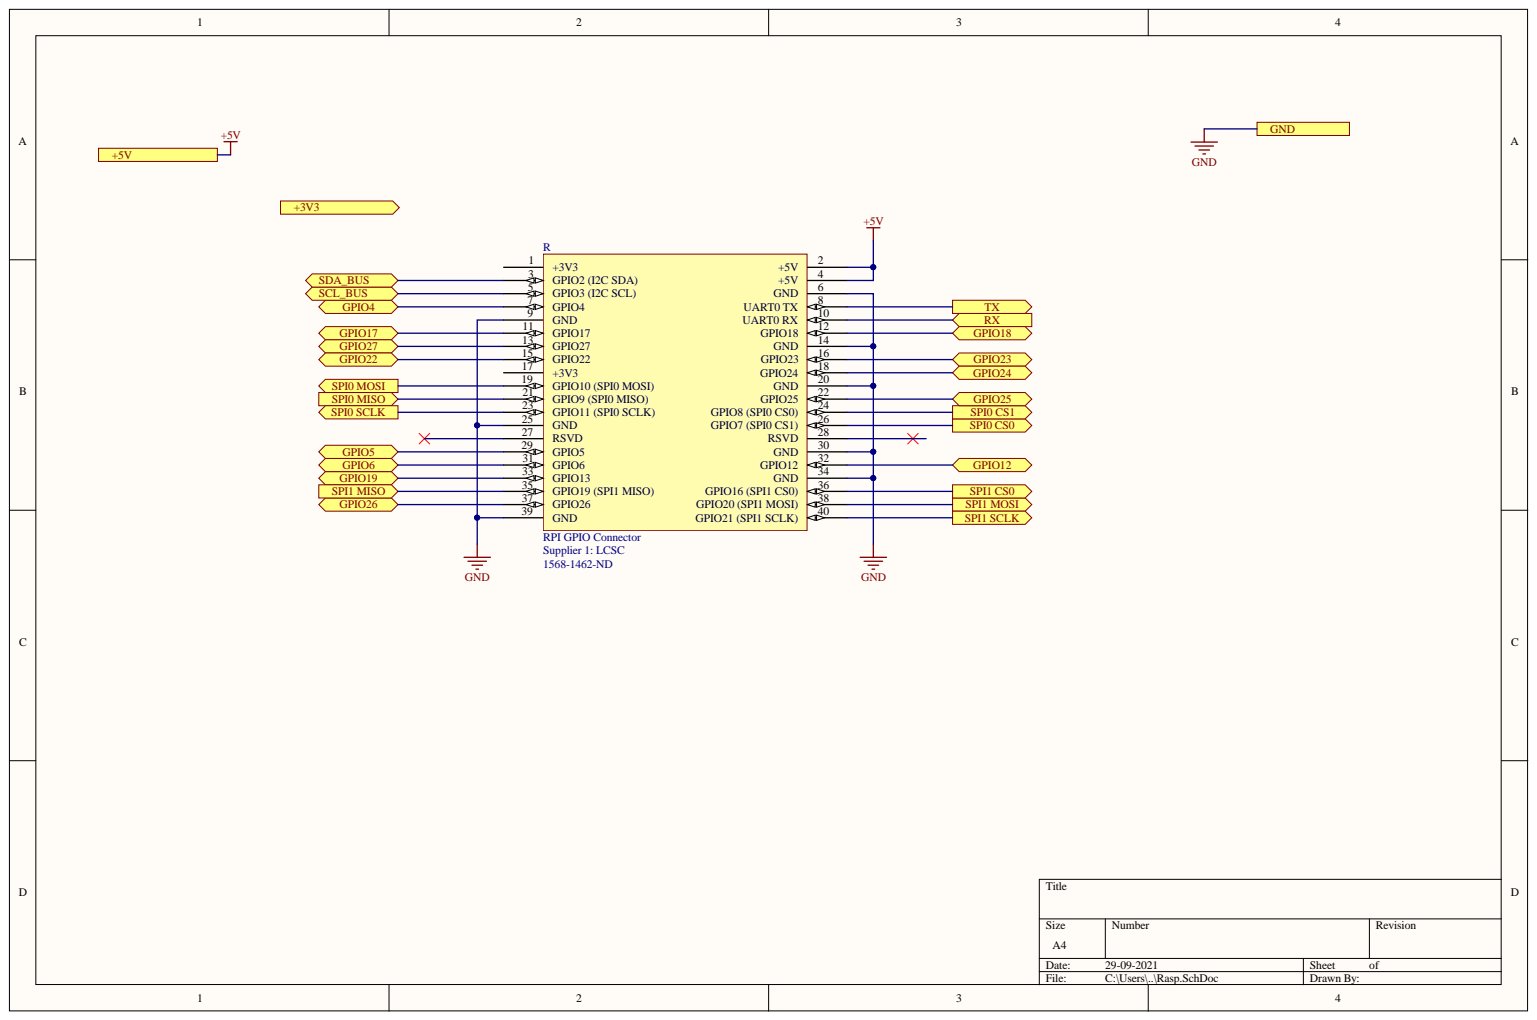
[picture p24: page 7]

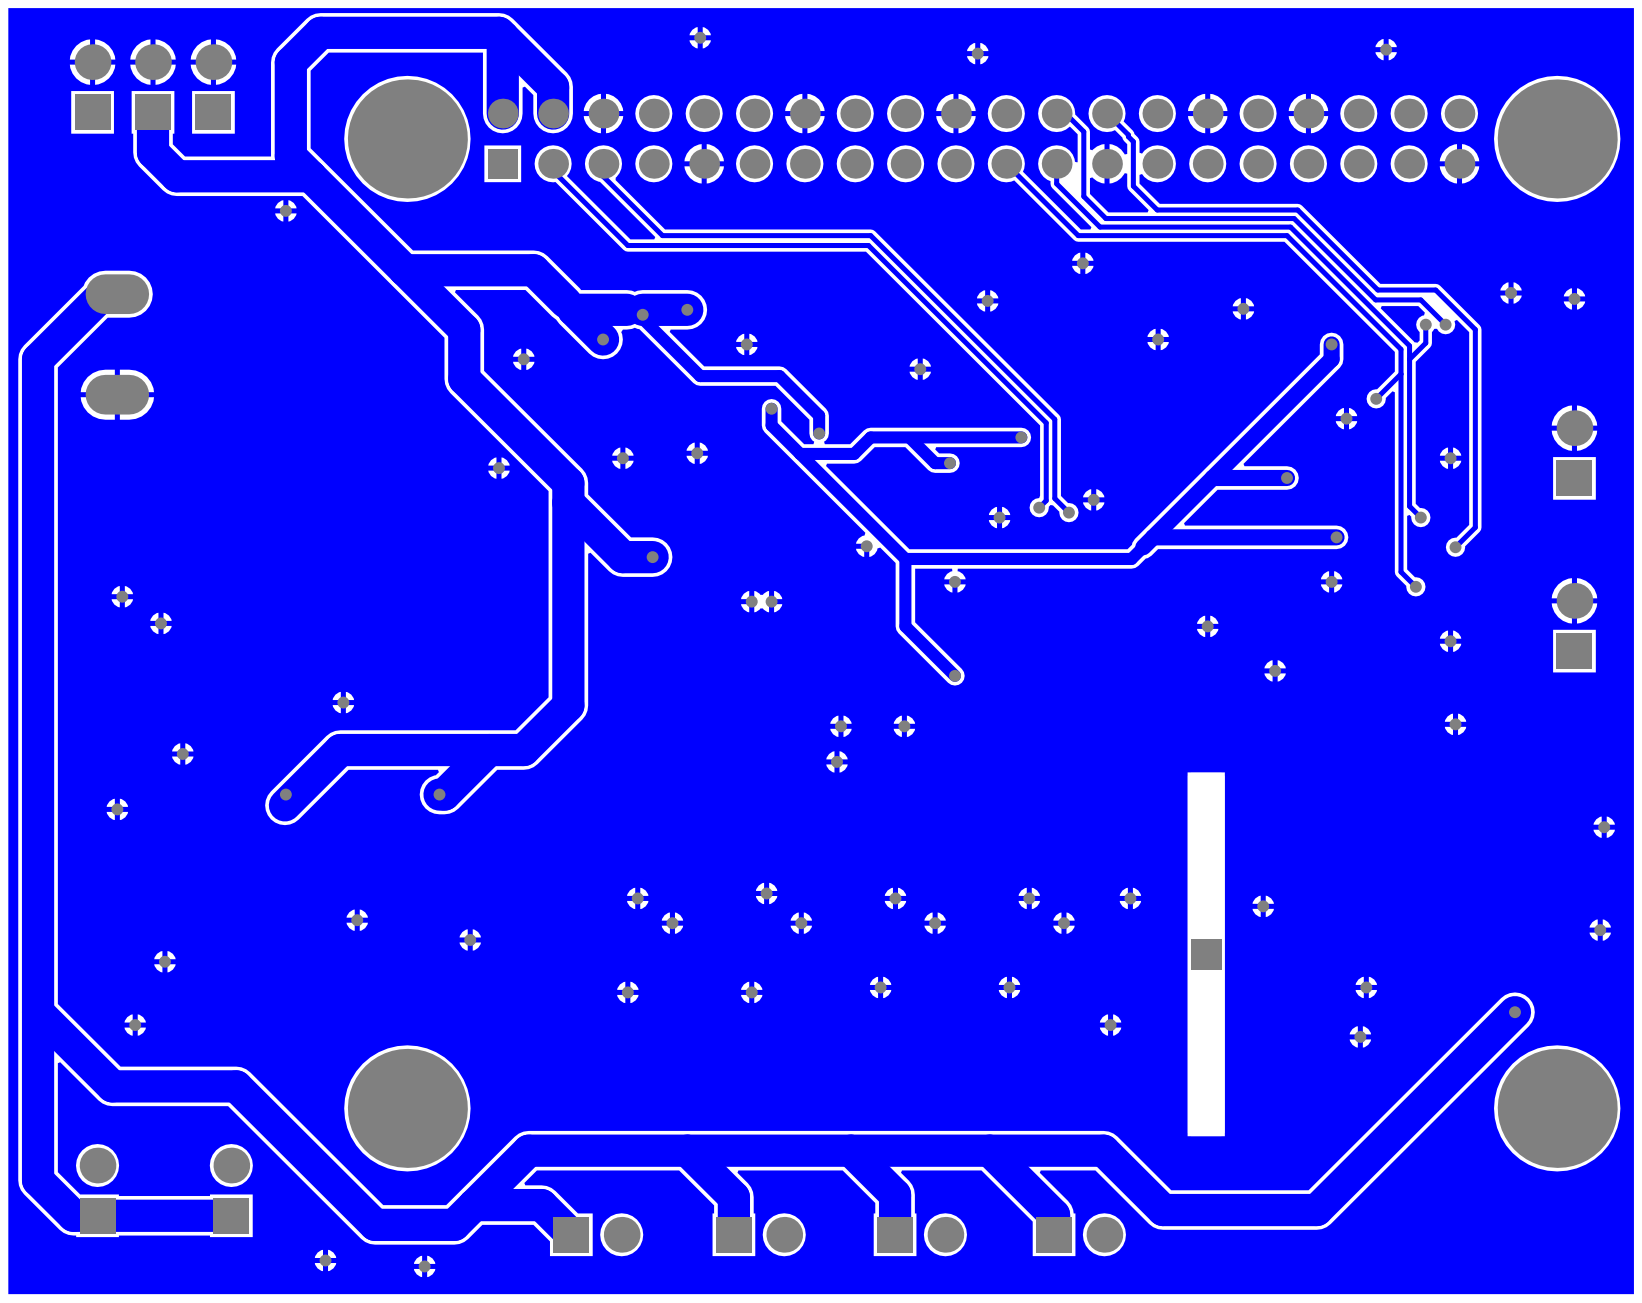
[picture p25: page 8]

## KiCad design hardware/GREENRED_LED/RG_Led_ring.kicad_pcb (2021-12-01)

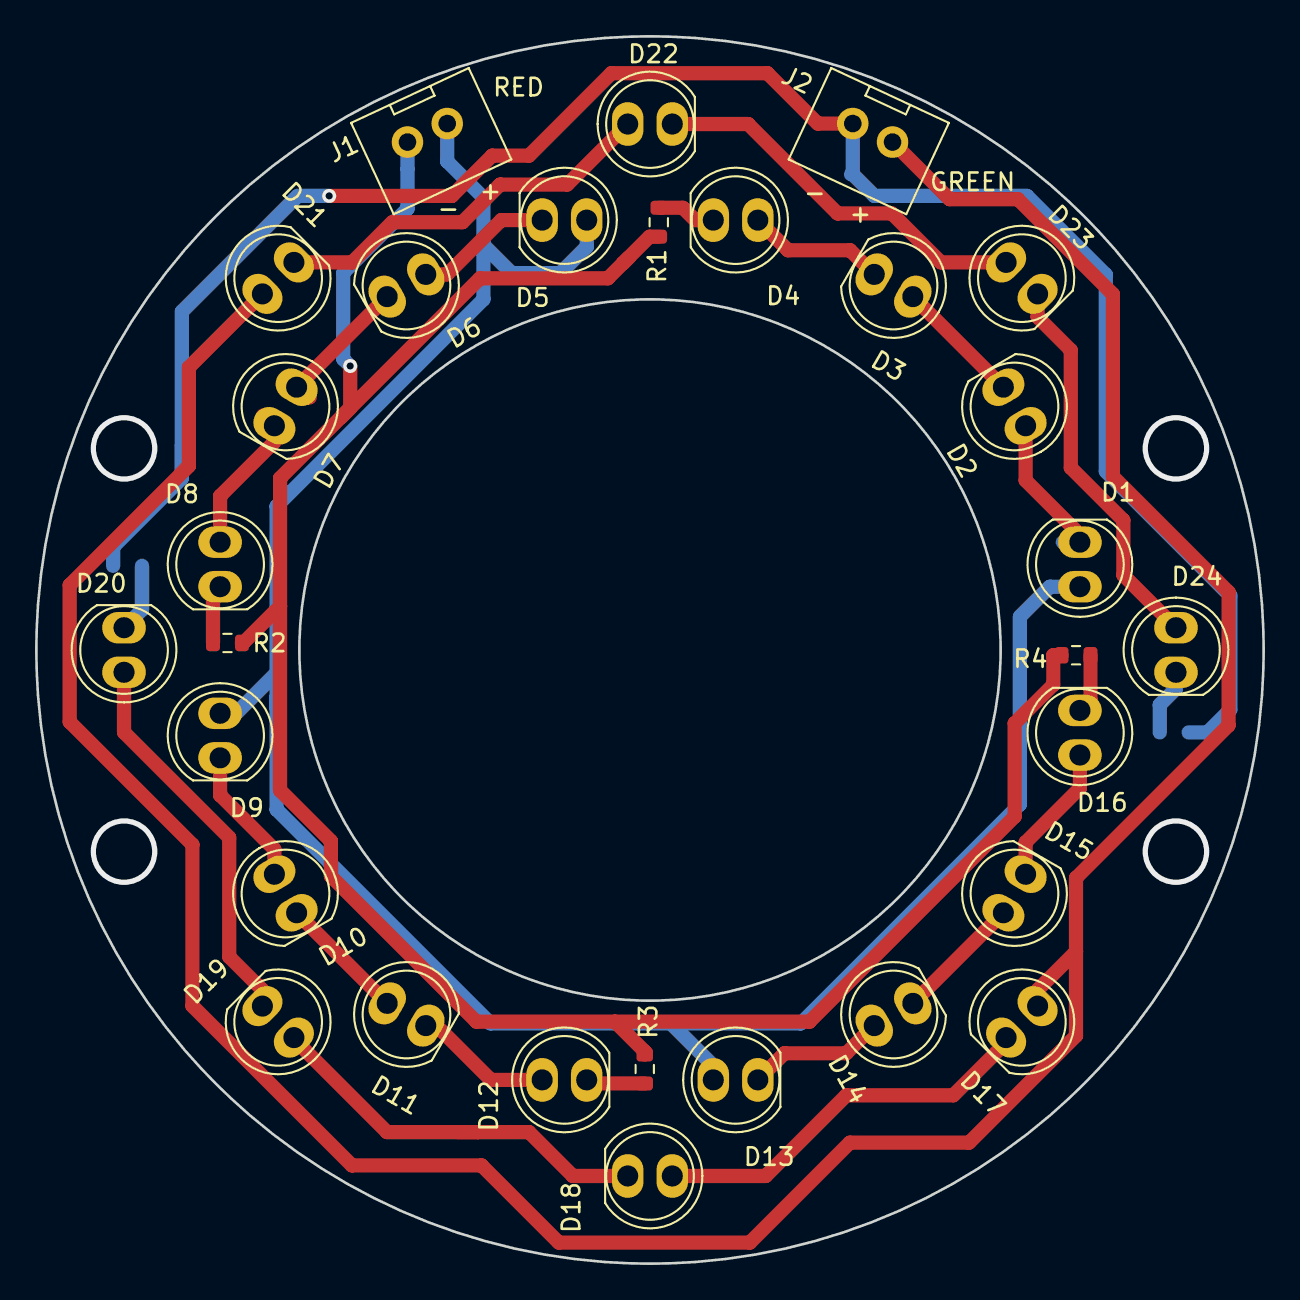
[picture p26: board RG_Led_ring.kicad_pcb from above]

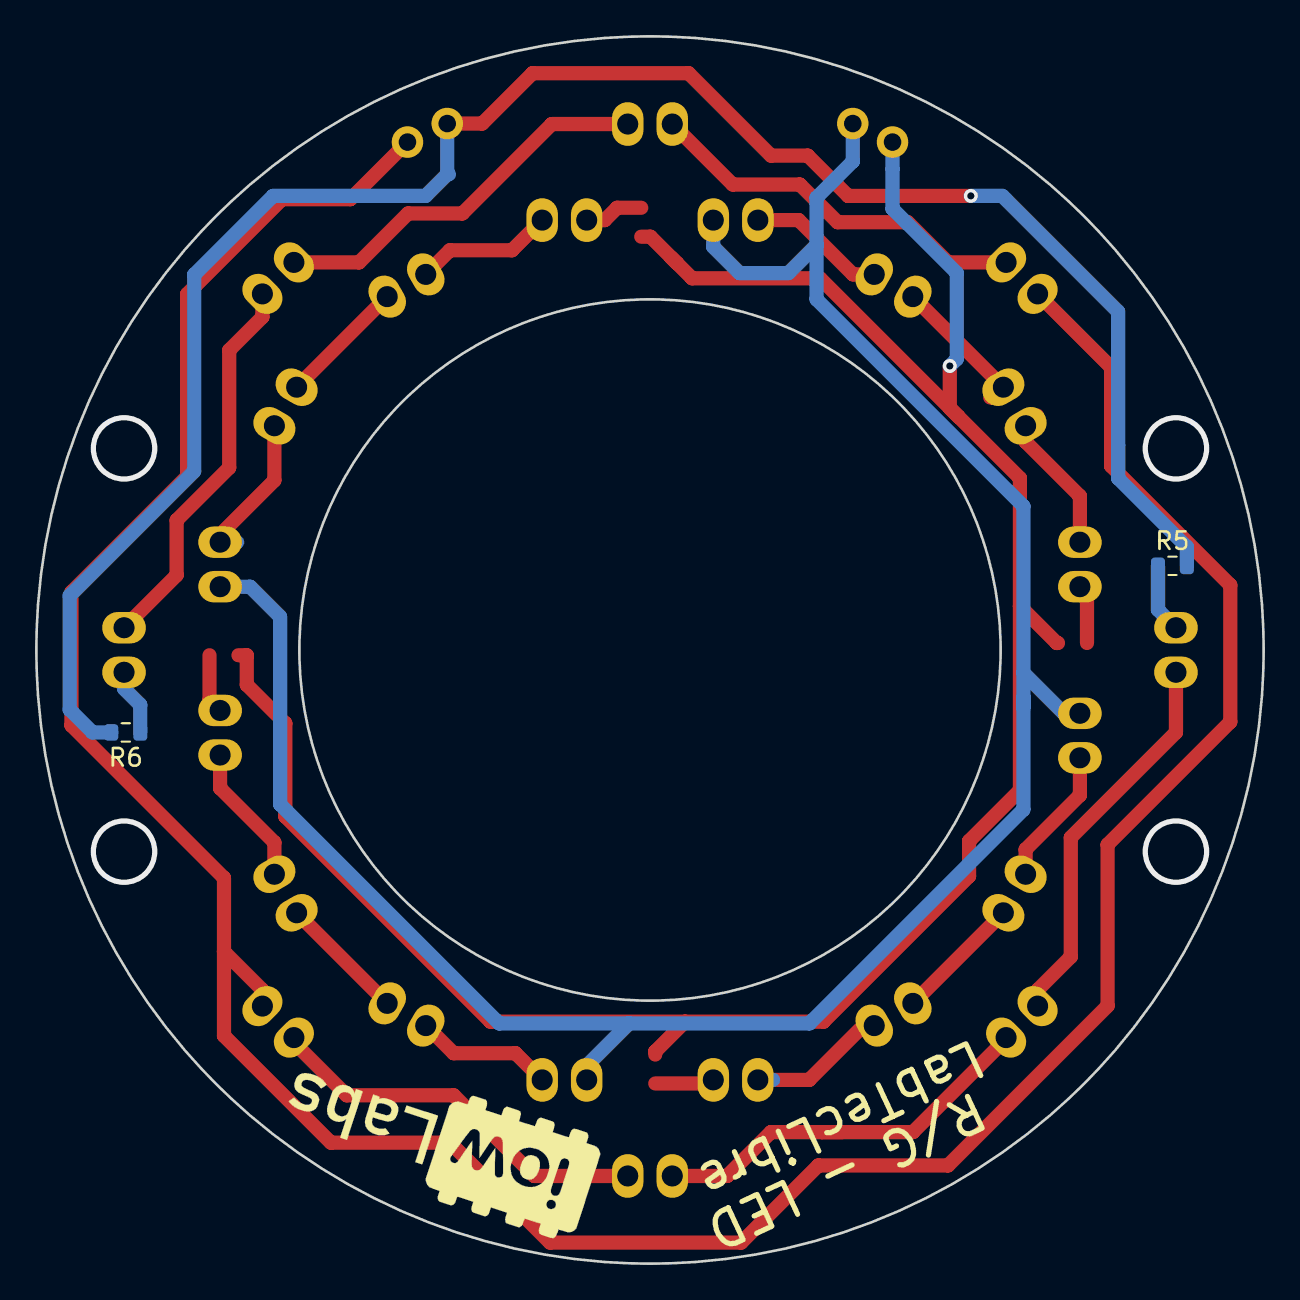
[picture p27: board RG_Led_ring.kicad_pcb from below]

Board: 2 copper layers, 70.0 x 70.0 mm, 32 parts (2 on the bottom side), 28 nets.

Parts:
D1, D2, D3, D4, D5, D6, D7, D8, D9, D10, D11, D12, D13, D14, D15, D16, D17, D18, D19, D20, D21, D22, D23, D24: LED; LED_5mm_TH_long
J1, J2: HDR-2x1; JST-XH-2x1-2.5p-TH-V
R1, R2, R3, R4, R5, R6: R_US; R_0603_1608Metric

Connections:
/LED_G+: D17.2, D21.2, J2.1
/LED_G-: J2.2, R5.2, R6.2
/LED_R+: D1.2, D5.2, D9.2, D13.2, J1.1
/LED_R-: J1.2, R1.2, R2.2, R3.2, R4.2
unnamed: D1.1, D2.2
unnamed: D2.1, D3.2
unnamed: D3.1, D4.2
unnamed: D4.1, R1.1
unnamed: D5.1, D6.2
unnamed: D6.1, D7.2
unnamed: D7.1, D8.2
unnamed: D8.1, R2.1
unnamed: D10.1, D11.2
unnamed: D9.1, D10.2
unnamed: D11.1, D12.2
unnamed: D12.1, R3.1
unnamed: D13.1, D14.2
unnamed: D14.1, D15.2
unnamed: D15.1, D16.2
unnamed: D16.1, R4.1
unnamed: D17.1, D18.2
unnamed: D18.1, D19.2
unnamed: D19.1, D20.2
unnamed: D20.1, R5.1
unnamed: D21.1, D22.2
unnamed: D22.1, D23.2
unnamed: D23.1, D24.2
unnamed: D24.1, R6.1

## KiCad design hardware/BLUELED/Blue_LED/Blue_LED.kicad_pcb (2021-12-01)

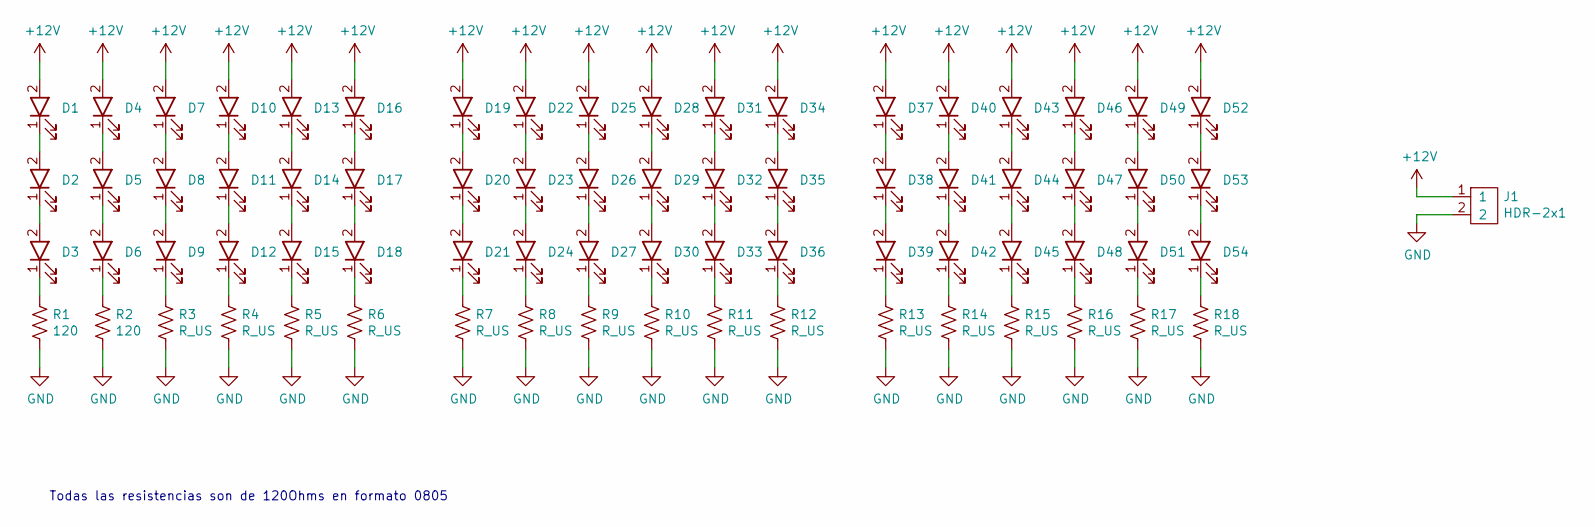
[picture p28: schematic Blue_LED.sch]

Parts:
D1, D2, D3, D4, D5, D6, D7, D8, D9, D10, D11, D12, D13, D14, D15, D16, D17, D18, D19, D20, D21, D22, D23, D24, D25, D26, D27, D28, D29, D30, D31, D32, D33, D34, D35, D36, D37, D38, D39, D40, D41, D42, D43, D44, D45, D46, D47, D48, D49, D50, D51, D52, D53, D54: LED; LED_5mm_TH_long
J1: HDR-2x1; JST-XH-2x1-2.5p-TH-V
R1, R2: 120; R_0805_2012Metric
R3, R4, R5, R6, R7, R8, R9, R10, R11, R12, R13, R14, R15, R16, R17, R18: R_US; R_0805_2012Metric

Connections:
+12V: D1.2, D4.2, D7.2, D10.2, D13.2, D16.2, D19.2, D22.2, D25.2, D28.2, D31.2, D34.2, D37.2, D40.2, D43.2, D46.2, D49.2, D52.2, J1.1
GND: J1.2, R1.2, R2.2, R3.2, R4.2, R5.2, R6.2, R7.2, R8.2, R9.2, R10.2, R11.2, R12.2, R13.2, R14.2, R15.2, R16.2, R17.2, R18.2
unnamed: D1.1, D2.2
unnamed: D2.1, D3.2
unnamed: D3.1, R1.1
unnamed: D4.1, D5.2
unnamed: D5.1, D6.2
unnamed: D6.1, R2.1
unnamed: D7.1, D8.2
unnamed: D8.1, D9.2
unnamed: D9.1, R3.1
unnamed: D10.1, D11.2
unnamed: D11.1, D12.2
unnamed: D12.1, R4.1
unnamed: D13.1, D14.2
unnamed: D14.1, D15.2
unnamed: D15.1, R5.1
unnamed: D16.1, D17.2
unnamed: D17.1, D18.2
unnamed: D18.1, R6.1
unnamed: D19.1, D20.2
unnamed: D20.1, D21.2
unnamed: D21.1, R7.1
unnamed: D22.1, D23.2
unnamed: D23.1, D24.2
unnamed: D24.1, R8.1
unnamed: D25.1, D26.2
unnamed: D26.1, D27.2
unnamed: D27.1, R9.1
unnamed: D28.1, D29.2
unnamed: D29.1, D30.2
unnamed: D30.1, R10.1
unnamed: D31.1, D32.2
unnamed: D32.1, D33.2
unnamed: D33.1, R11.1
unnamed: D34.1, D35.2
unnamed: D35.1, D36.2
unnamed: D36.1, R12.1
unnamed: D37.1, D38.2
unnamed: D38.1, D39.2
unnamed: D39.1, R13.1
unnamed: D40.1, D41.2
unnamed: D41.1, D42.2
unnamed: D42.1, R14.1
unnamed: D43.1, D44.2
unnamed: D44.1, D45.2
unnamed: D45.1, R15.1
unnamed: D46.1, D47.2
unnamed: D47.1, D48.2
unnamed: D48.1, R16.1
unnamed: D49.1, D50.2
unnamed: D50.1, D51.2
unnamed: D51.1, R17.1
unnamed: D52.1, D53.2
unnamed: D53.1, D54.2
unnamed: D54.1, R18.1

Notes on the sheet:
Todas las resistencias son de 120Ohms en formato 0805

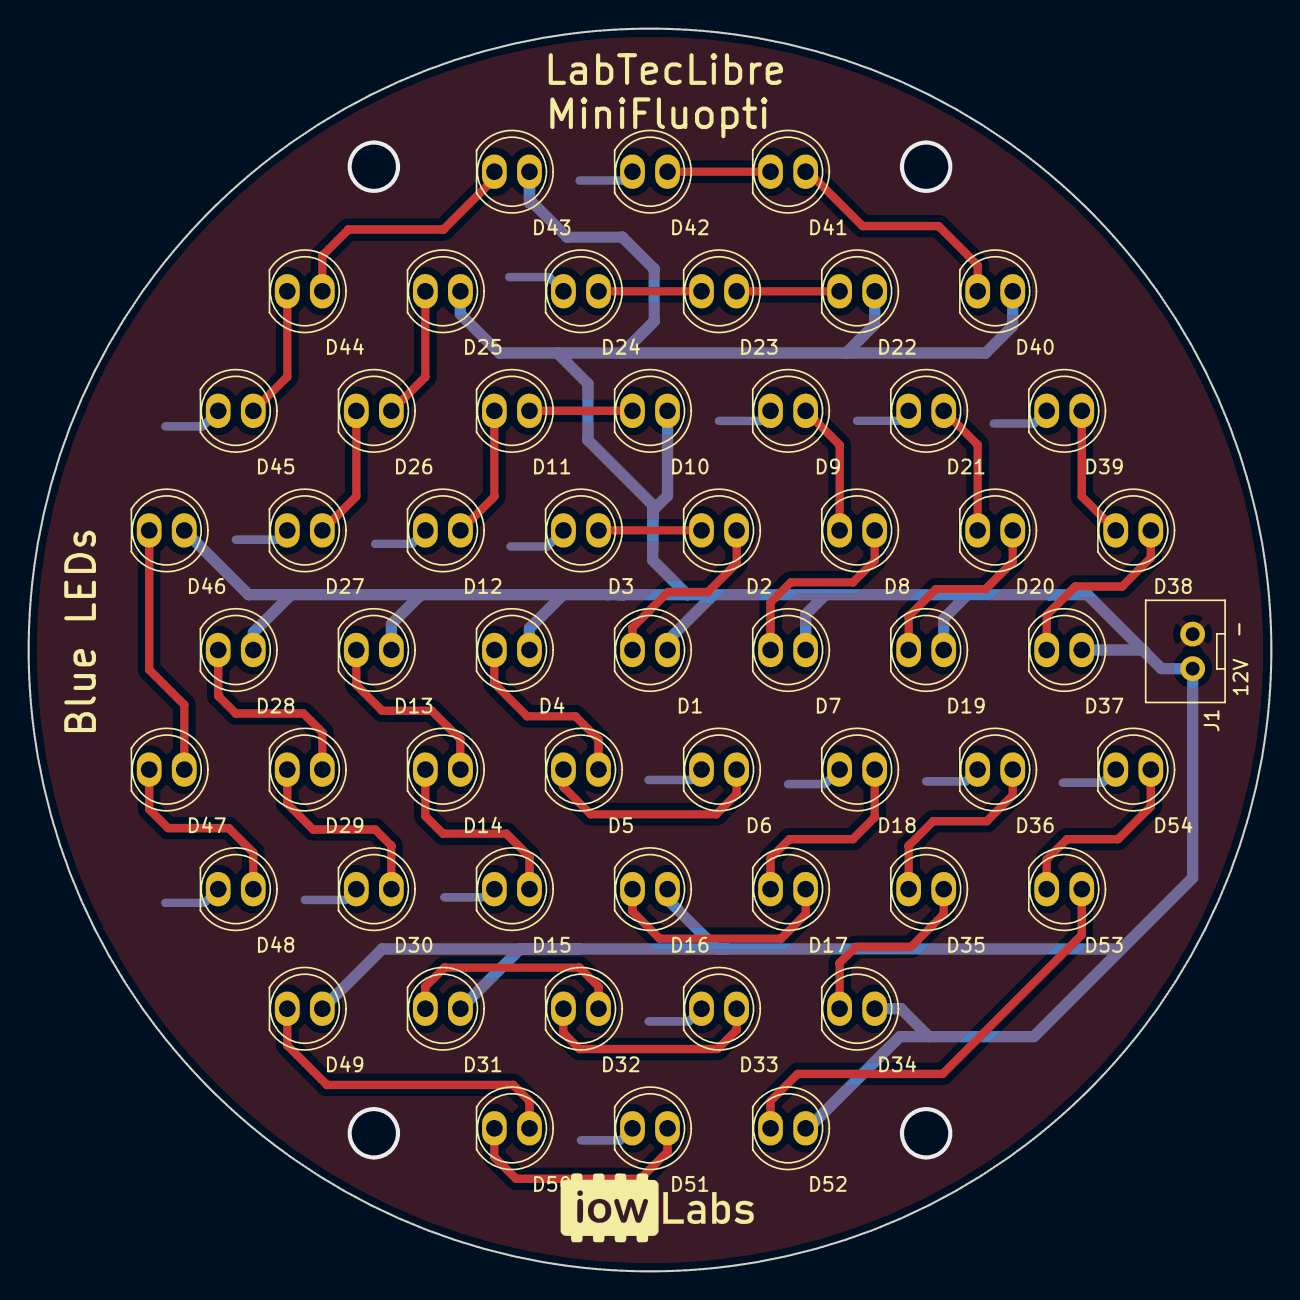
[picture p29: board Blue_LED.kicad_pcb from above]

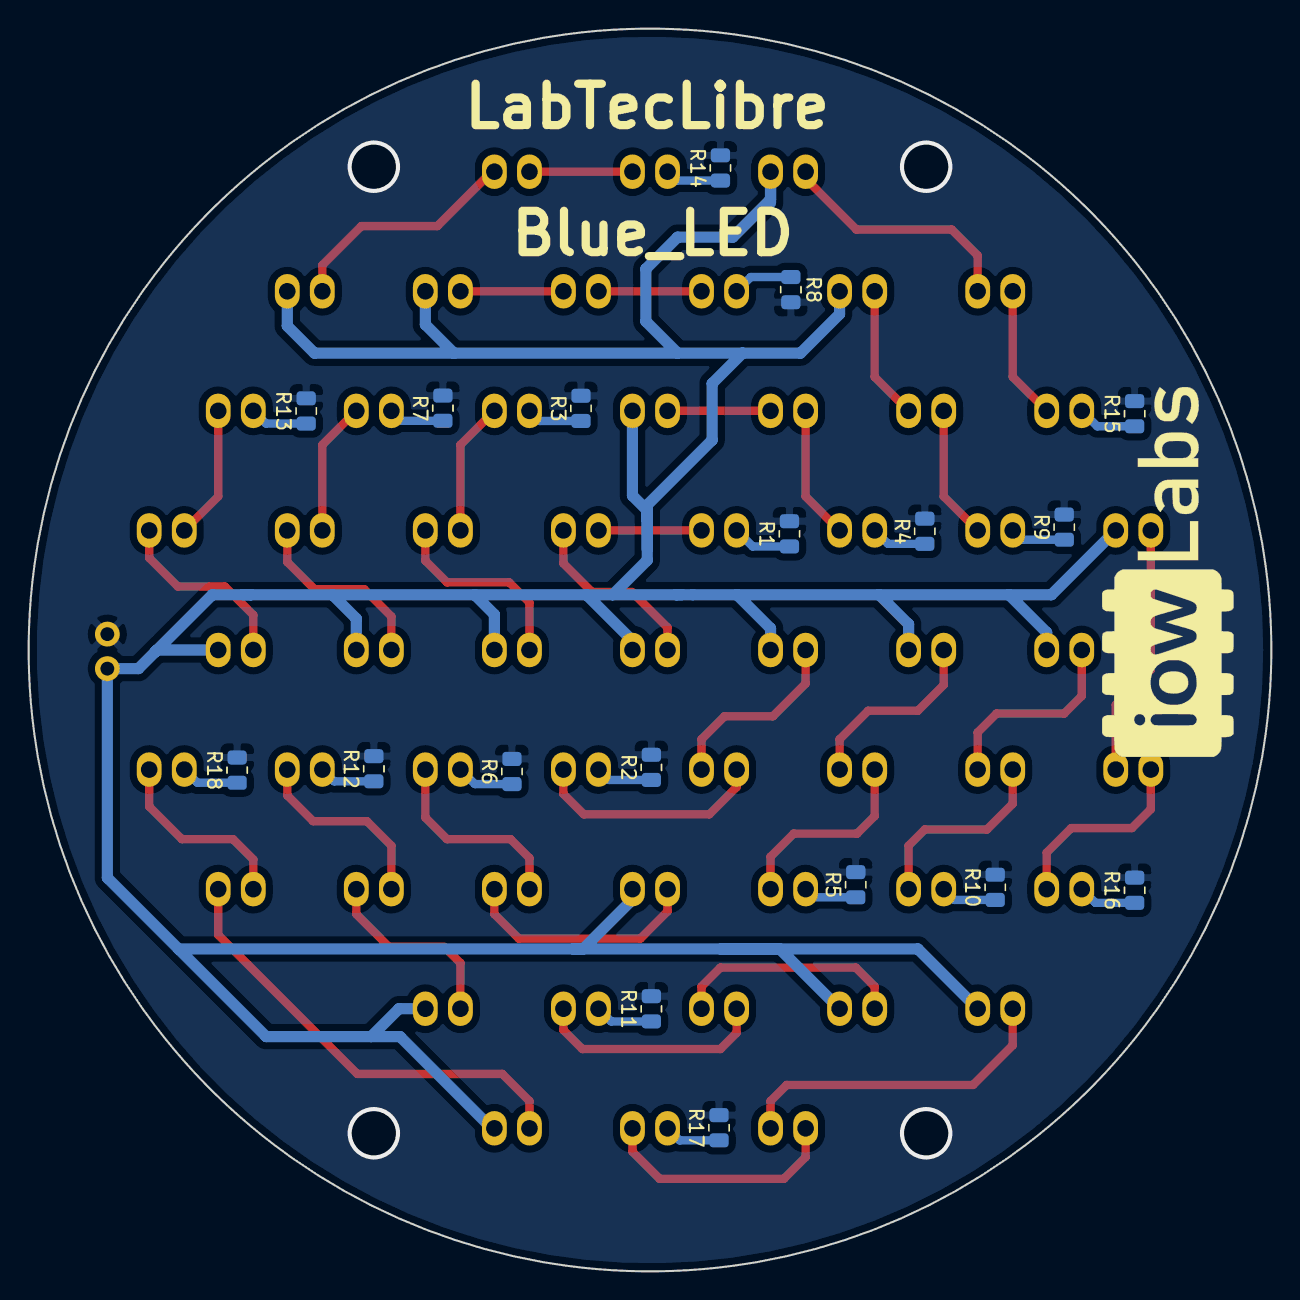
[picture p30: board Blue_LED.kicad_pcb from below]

Board: 2 copper layers, 90.0 x 90.0 mm, 73 parts (18 on the bottom side), 56 nets.

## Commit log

2021-04-06 FluOpti PCB added
    [ADC.SchDoc, ConectoresEntrada.SchDoc, ConectoresSalida.SchDoc, DCDC_stepdown.SchDoc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]
2021-04-07 schematic updated
    [ADC.SchDoc, ConectoresEntrada.SchDoc, ConectoresSalida.SchDoc, DCDC_stepdown.SchDoc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]
2021-04-08 pcb design
    [ConectoresEntrada.SchDoc, ConectoresSalida.SchDoc, Drivers.SchDoc, PCB1.PcbDoc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]
2021-04-12 changes updated
    [ADC.SchDoc, ConectoresEntrada.SchDoc, ConectoresSalida.SchDoc, DCDC_stepdown.SchDoc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]
2021-04-16 adding readme
    [ADC.SchDoc, ConectoresEntrada.SchDoc, ConectoresSalida.SchDoc, DCDC_stepdown.SchDoc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]
2021-08-28 Add MiniFluOpti board and blue led board
    [ADC.SchDoc, Blue LED.PrjPcb, BlueLed.SchDoc, ConectoresEntrada.SchDoc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]
2021-09-03 minor changes
    [ADC.SchDoc, Bill of Materials-PCB1.xls, ConectoresSalida.SchDoc, DCDC_stepdown.SchDoc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]
2021-09-29 adding pdf
    [ADC.SchDoc, Bill of Materials-PCB1.xls, ConectoresSalida.SchDoc, DCDC_stepdown.SchDoc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]
2021-10-01 adding some datasheets
    [miniFOdriver_V1.0.PrjPcb]
2021-12-01 adding ntc functions
    [Blue_LED-B_Cu.gbl, Blue_LED-B_Mask.gbs, Blue_LED-B_Paste.gbp, Blue_LED-B_SilkS.gbo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]
2021-12-01 removing debug prints from pi_ntc
2023-08-31 testing leds
2023-09-09 gui v2
    [ADC.SchDoc, Bill of Materials-PCB1.xls, Blue LED.PrjPcb, BlueLed.SchDoc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]
2023-10-10 MiniFluOpti first enclosure prototype
    [Flat_cam_holder.scad, Flat_cam_holder_WS.stl, V2_filter_holder_thread.scad, V2_filter_holder_thread.stl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]
2023-11-13 add measurements to RGLED board and related svg and png files
2023-12-19 update the open scad file to create all the 3D componentes of the camera support and LED ring enclosure
    [Flat_cam_holder.scad]
2024-01-25 include the RPIv2 camera option for the flat cam holder. Organize files and include STLs and gCodes
    [Flat_cam_holder.scad, Flat_cam_holder_HQ.stl, Flat_cam_holder_V2.stl, Flat_cam_holder_WS.stl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]
